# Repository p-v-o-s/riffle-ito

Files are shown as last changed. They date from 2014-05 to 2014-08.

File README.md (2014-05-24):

riffle-ito
=========

The RIFFLE-ito is a lower-functionality and higher cost version of the [Riffle](http://publiclab.org/wiki/riffle) water quality sensor. The Riffle-ito is based on the Atmel328p, and is intended to be compatible with the accessibile and ubiquitous Wiring platform (and, by extension, the Arduino IDE). For a lower-cost, higher-functionalty Riffle that isn't yet compatible with Wiring, please see [here](https://github.com/bgamari/riffle). 

The width and height of the Riffle-ito device allows the device to fit through the mouth of a standard commercially produced plastic water bottle (20 mm). By inserting the Riffle-ito into such a bottle, along with a few AA batteries, and connecting a thermistor and other sensors that poke out through the water bottle cap, a very accessible water quality sensor may be constructed. 

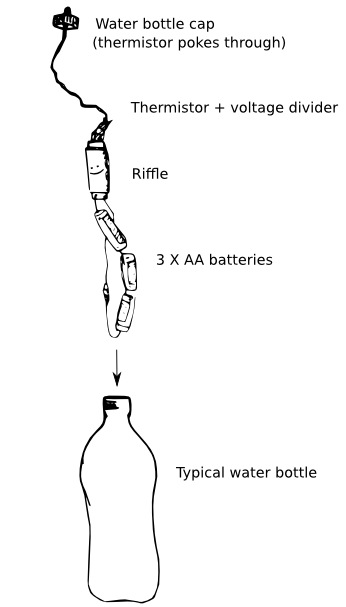
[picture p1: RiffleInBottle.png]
Optional title


Details:

- the Riffle-ito requires an [FTDI cable](https://www.adafruit.com/products/284) in order to be reprogrammed (e.g. Adafruit's [FTDI Friend](https://www.adafruit.com/products/284) or SparkFun's ['FTDI Basic Breakout'](https://www.sparkfun.com/products/9716)), which typically costs $15 or so. One cable can be used for several Riffle-ito senso nodes.
- includes a uSD holder, I2C EEPROM flash memory, and a high-precision real time clock (the DS3231) with coin battery backup
- programmable as an "Arduino UNO" board in the Arduino IDE
- runs at 3.3V / 16 MHz
- includes circuit for monitoring battery level
- the board width (18 mm) and height profile (uses right-angle headers) allows device to be inserted through mouth of standard plastic water bottle (one with 20 mm diameter or greater)
- Rough estimate of the total cost of parts that could be used to log temperature in a water bottle (not including shipping, the water bottle, or an FTDI cable): 38 USD;  a detailed cost estimate is [here](https://docs.google.com/spreadsheets/d/1v0O8HmP8-q_kPunHILv5Io3zThpqvPBZZoY3aYnxRDc/edit#gid=0)
- For a diagram of pin locations and optional configurations, please see this [diagram in PDF format](https://github.com/p-v-o-s/riffle328/blob/master/riffleUsage.pdf)

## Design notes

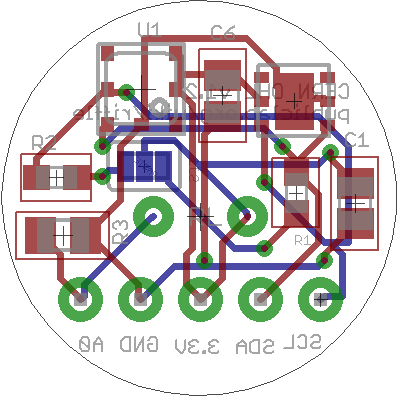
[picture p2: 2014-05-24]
hardware/riffleito-THPL-REVB-board.png

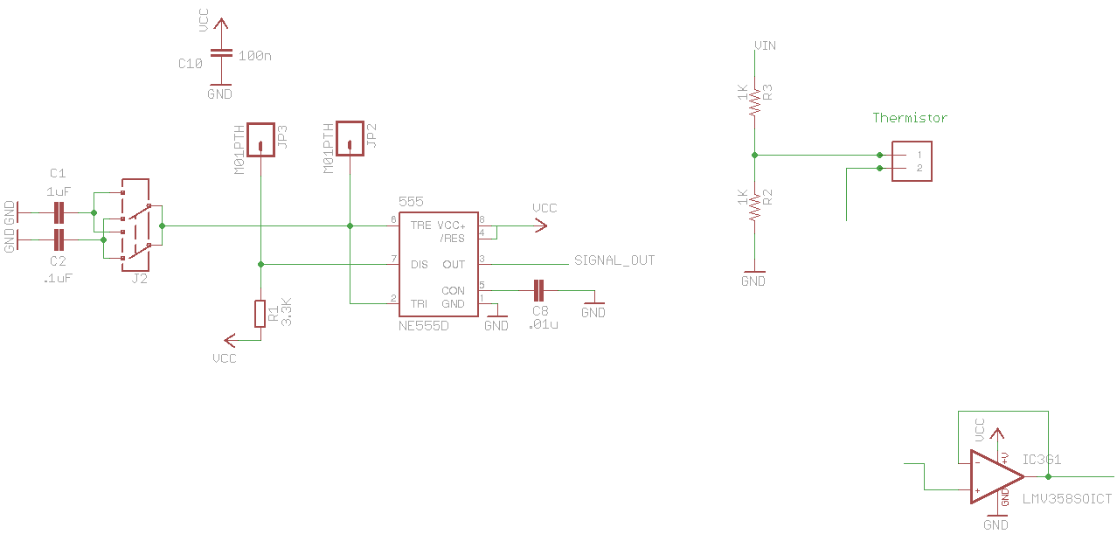
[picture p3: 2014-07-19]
hardware/conduct3-schem.png

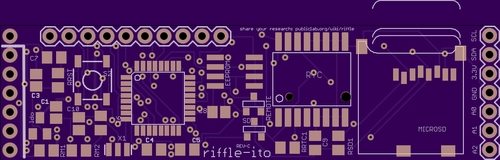
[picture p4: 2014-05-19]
hardware/riffle-ito-revc-osh-front.png

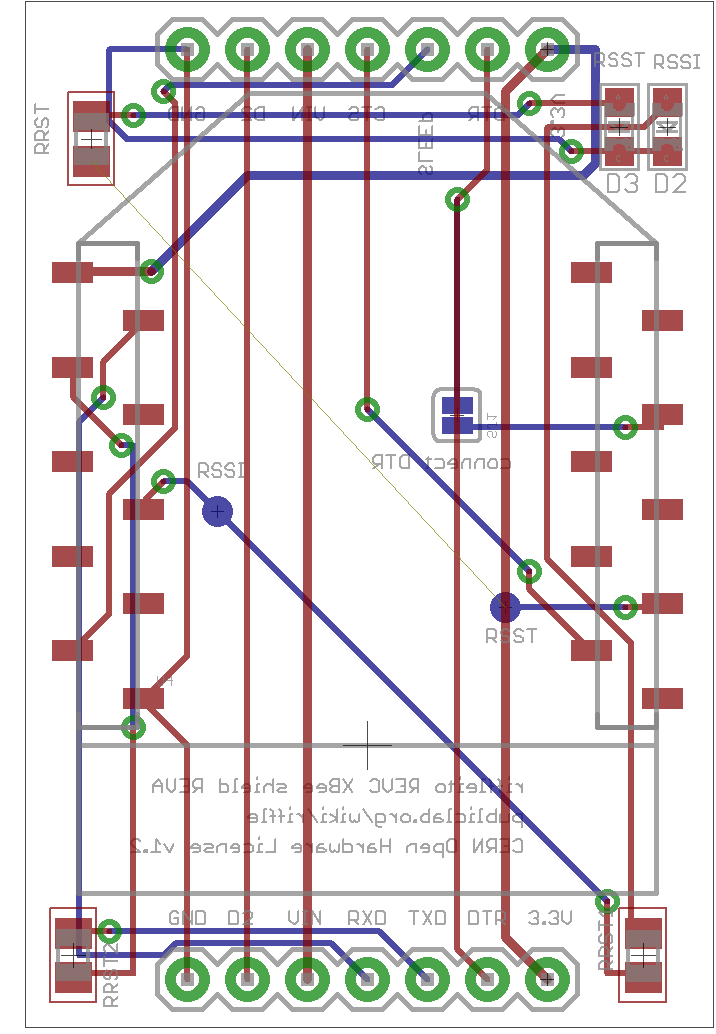
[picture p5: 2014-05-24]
hardware/riffleito-Xbee_REVA-board.png

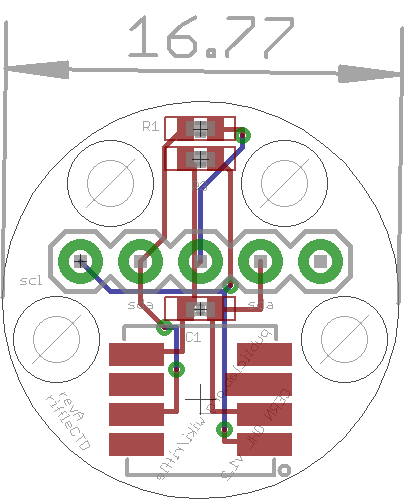
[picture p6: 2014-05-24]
hardware/riffleito-CTD-REVA-board.png

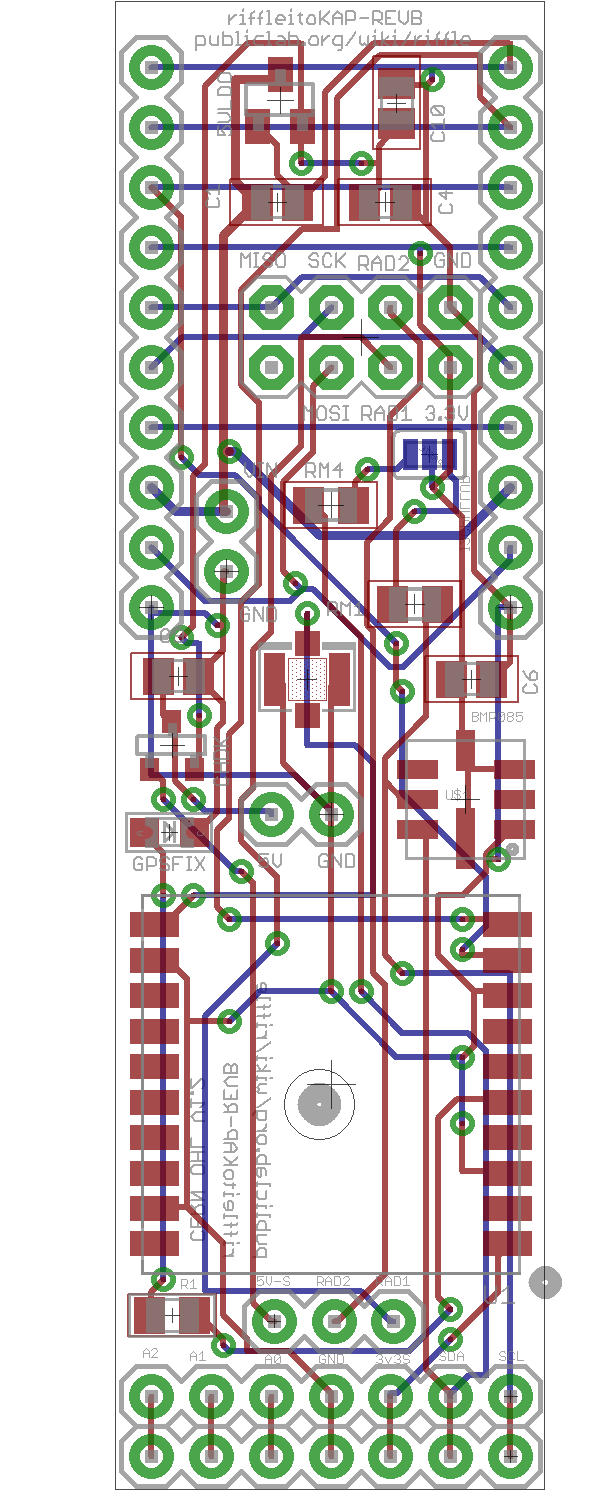
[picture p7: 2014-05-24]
hardware/riffleito-KAP-REVB-board.png

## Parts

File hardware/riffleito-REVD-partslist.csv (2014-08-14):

Part | Value | Device | Package | Description | MF | MPN | OC_FARNELL | OC_NEWARK
BAT | CR1220 | BATTERYBATTERY_12MM_SMT | BATTCON_12MM_SMT | Battery Holders
C1 | 10u | C-EUC0805 | C0805 | CAPACITOR, European symbol
C3 | 10u | C-EUC0805 | C0805 | CAPACITOR, European symbol
C4 | 0.1uF | C-EUC0805 | C0805@1 | CAPACITOR, European symbol
C5 | 0.1uF | C-EUC0805 | C0805@1 | CAPACITOR, European symbol
C6 | .1uF | C-EUC0805 | C0805@1 | CAPACITOR, European symbol
C7 | 0.1uF | C-EUC0805 | C0805@1 | CAPACITOR, European symbol
C8 | .1u | C-EUC0805 | C0805 | CAPACITOR, European symbol
C10 | .1u | C-EUC0805 | C0805 | CAPACITOR, European symbol
CRF | .1u | C-EUC0805 | C0805 | CAPACITOR, European symbol
CSD | .1uF | C-EUC0805 | C0805 | CAPACITOR, European symbol
I2C1 | 10K | R-EU_R0805 | R0805 | RESISTOR, European symbol
I2C2 | 10K | R-EU_R0805 | R0805 | RESISTOR, European symbol
IC1 | ATMEGA328P | MEGA8-AI | TQFP32-08 | MICROCONTROLLER |  | ATMEGA8-16AU | 9171371 | 73M8863
IC2 | 24AA128SN | 24AA128SN | SO-08 | Serial EEPROM | MICROCHIP | 24AA128-I/SN | unknown | 92C6842
IC4 | MCP1700-33 | MCP1700SOT233 | SOT23 | VOLTAGE REGULATOR
JP1 |  | M081X08 | 1X08 | Header 8
JP2 |  | M06SIP | 1X06 | Header 6
JP4 |  | M07 | 1X07 | Header 7
MICROSD | MICROSD | MICROSD | MICROSD | Micro-SD / Transflash card holder with SPI pinout
REMOTE | FDN340P | PMOSSOT23 | SOT-23 | MOS FET
RM1 | 10K | R-EU_R0805 | R0805 | RESISTOR, European symbol
RM2 | 10K | R-EU_R0805 | R0805 | RESISTOR, European symbol
RRST | 10K | R-EU_R0805 | R0805 | RESISTOR, European symbol
RRTC1 | 10K | R-EU_R0805 | R0805 | RESISTOR, European symbol
RSD1 | 10K | R-EU_R0805 | R0805 | RESISTOR, European symbol
RTC | DS3231 | DS3231 | DS3231
RTCINT | SOLDERJUMPERNO | SOLDERJUMPERNO | SJ_2S-NO | Solder Jumper
SD | FDN340P | PMOSSOT23 | SOT-23 | MOS FET
U$1 | M04X2 | M04X2 | 2X4 | .1 header, two rows of four."
X1 | 16 MHz | RESONATORSMD | RESONATOR-SMD | Resonator

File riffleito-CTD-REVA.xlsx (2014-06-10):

Part | Value | Device | Package | Description
C1 | 100 nF | CAP0402-CAP | 0402-CAP | Capacitor
JP2 |  | M05PTH | 1X05 | Header 5
MS5803 | MS5803-14BA | MS5803-14BA | MS5803-14BA
R1 | 10K | RESISTOR0402-RES | 0402-RES | Resistor
R3 | 10K | RESISTOR0402-RES | 0402-RES | Resistor

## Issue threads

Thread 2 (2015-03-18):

### ISSUE TITLE
Make 'Nutrition Facts' label

### ISSUE THREAD

**Issue by dwblair** [p-v-o-s/riffle-ito#2]
![rifflelabel](https://cloud.githubusercontent.com/assets/639760/3027999/30445cfa-e028-11e3-8816-b8fbdc38216b.png)

**Comment by BobStevens** [comment]
perhaps a vintage beverage logo...
![riffle](https://cloud.githubusercontent.com/assets/4740637/3029463/75da4e70-e035-11e3-9c63-8aa23d116dfc.png)
![riffle2](https://cloud.githubusercontent.com/assets/4740637/3032722/72b22f80-e05b-11e3-9458-ed36393352e9.png)

**Comment by dwblair** [comment]
Bob.  You're a genius.  MAJORLY AWESOME.

**Comment by kanarinka** [comment]
![rifflelabel2](https://cloud.githubusercontent.com/assets/1102550/3116949/32e98ee2-e723-11e3-82cc-9f281cf4ee9f.png)
Another label idea!! Let's keep iterating and then we can make a couple and do market research on which label seduces the most citizen scientists :+1:

**Comment by kanarinka** [comment]
![rifflelabel3](https://cloud.githubusercontent.com/assets/1102550/3117523/aab2b39e-e72e-11e3-8b7b-fed8c4b8d51d.png)
And here's one using Bob's font which I like a great deal!

**Comment by kanarinka** [comment]
![rifflelabel4](https://cloud.githubusercontent.com/assets/1102550/3117865/ece08718-e734-11e3-8b70-3ab5bd1f3163.png)
What about this for the water bottle conference stickers?? I'd have to redo it more carefully and not sure if the bleed would work but let me know

**Comment by BobStevens** [comment]
Nice, the font I used is an open font called Lemon by Eduardo Tunni.

**Comment by kanarinka** [comment]
❤️❤️❤️😄

El miércoles, 18 de marzo de 2015, dwblair notifications@github.com
escribió:

> Closed #2 https://github.com/p-v-o-s/riffle-ito/issues/2.
> 
> —
> Reply to this email directly or view it on GitHub
> https://github.com/p-v-o-s/riffle-ito/issues/2#event-258748090.

## 

---

www.kanarinka.com    ||    kanarinka@ikatun.org    ||    617-501-2441

---

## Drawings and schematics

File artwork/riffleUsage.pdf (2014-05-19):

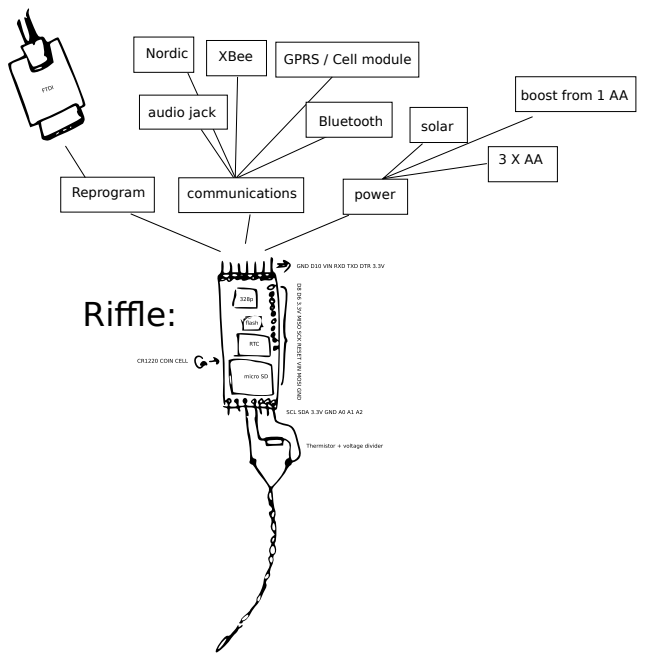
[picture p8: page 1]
Bluetooth; Riffle:; XBee; GPRS / Cell module; power; solar; Reprogram; Nordic; communications; audio jack

boost from 1 AA

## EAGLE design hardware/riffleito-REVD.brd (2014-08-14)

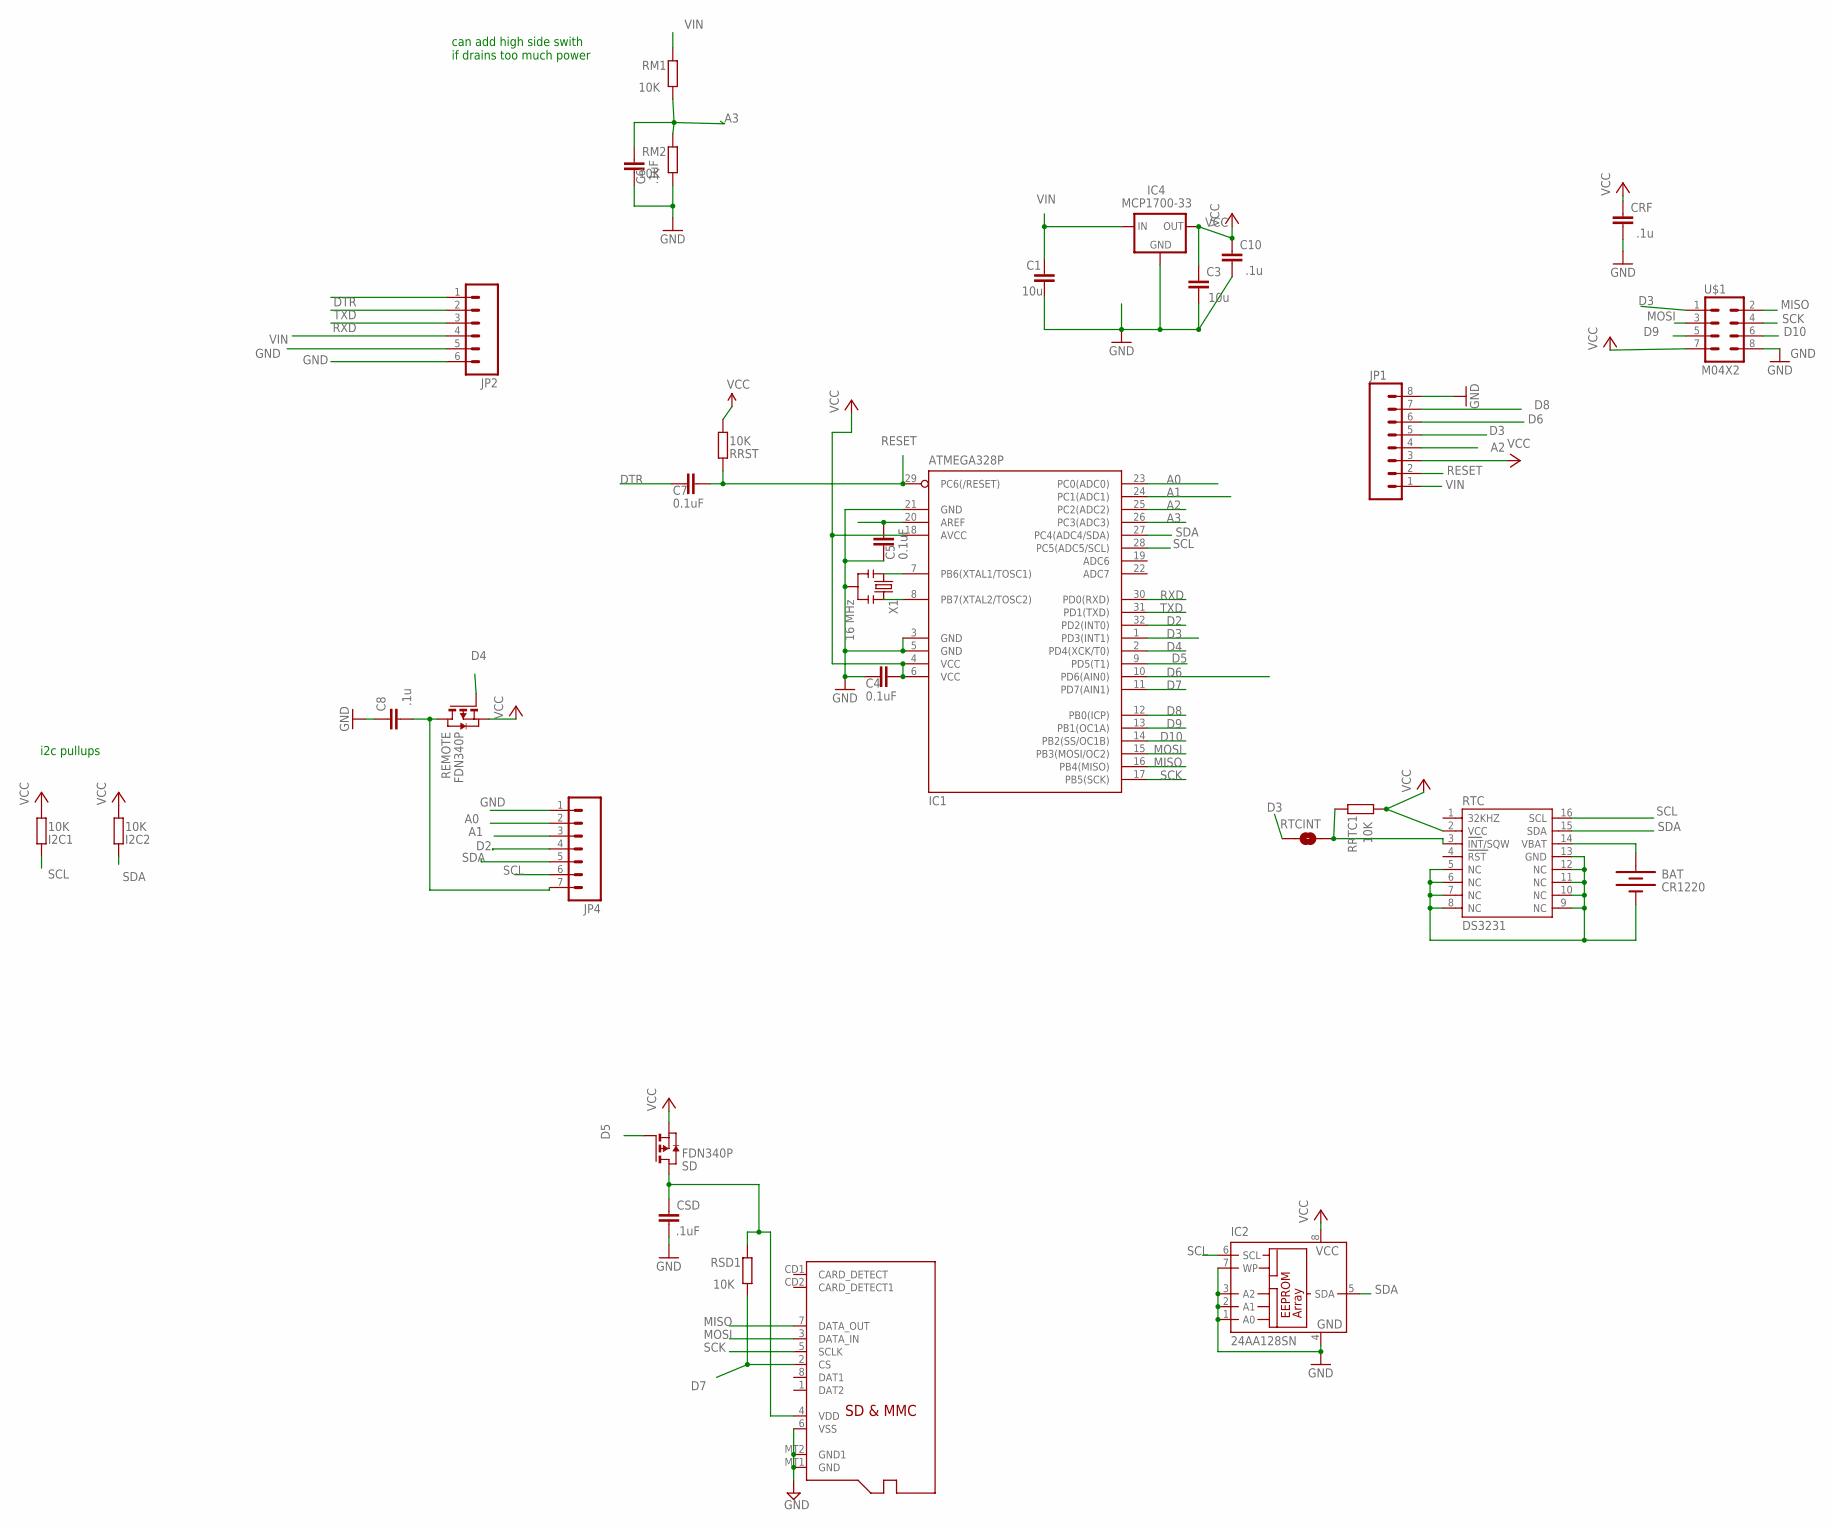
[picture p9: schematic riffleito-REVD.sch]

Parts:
BAT: CR1220; BATTCON_12MM_SMT
C1, C3: 10u; C0805
C4, C5, C7: 0.1uF; C0805@1
C6: .1uF; C0805@1
C8, C10: .1u; C0805
CRF: .1u; C0805
CSD: .1uF; C0805
I2C1, I2C2: 10K; R0805
IC1: ATMEGA328P; TQFP32-08
IC2: 24AA128SN; SO-08
IC4: MCP1700-33; SOT23
JP1: M081X08; 1X08
JP2: M06SIP; 1X06
JP4: M07; 1X07
MICROSD: MICROSD
REMOTE: FDN340P; SOT-23
RM1, RM2: 10K; R0805
RRST: 10K; R0805
RRTC1: 10K; R0805
RSD1: 10K; R0805
RTC: DS3231
RTCINT: SOLDERJUMPERNO; SJ_2S-NO
SD: FDN340P; SOT-23
U$1: M04X2; 2X4
X1: 16 MHz; RESONATOR-SMD

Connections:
A0: IC1.23 (PC0(ADC0)), JP4.2
A1: IC1.24 (PC1(ADC1)), JP4.3
A2: IC1.25 (PC2(ADC2)), JP1.4
A3: C6.2, IC1.26 (PC3(ADC3)), RM1.1, RM2.2
AREF: C5.2, IC1.20 (AREF)
D2: IC1.32 (PD2(INT0)), JP4.4
D3: IC1.1 (PD3(INT1)), JP1.5, RTCINT.2, U$1.1
D4: IC1.2 (PD4(XCK/T0)), REMOTE.3 (G)
D5: IC1.9 (PD5(T1)), SD.3 (G)
D6: IC1.10 (PD6(AIN0)), JP1.6
D7: IC1.11 (PD7(AIN1)), MICROSD.2 (CS), RSD1.1
D8: IC1.12 (PB0(ICP)), JP1.7
D9: IC1.13 (PB1(OC1A)), U$1.5
D10: IC1.14 (PB2(SS/OC1B)), U$1.6
DTR: C7.1, JP2.1
GND: BAT.P$1 (-), C1.2, C3.2, C4.1, C5.1, C6.1, C8.1, C10.2, CRF.2, CSD.2, IC1.3 (GND), IC1.5 (GND), IC1.21 (GND), IC2.1 (A0), IC2.2 (A1), IC2.3 (A2), IC2.4 (GND), IC2.7 (WP), IC4.1 (GND), JP1.8, JP2.5, JP2.6, JP4.1, MICROSD.6 (VSS), MICROSD.MT1 (GND), MICROSD.MT2 (GND1), RM2.1, RTC.5 (NC), RTC.6 (NC), RTC.7 (NC), RTC.8 (NC), RTC.9 (NC), RTC.10 (NC), RTC.11 (NC), RTC.12 (NC), RTC.13 (GND), U$1.8, X1.2
MISO: IC1.16 (PB4(MISO)), MICROSD.7 (DATA_OUT), U$1.2
MOSI: IC1.15 (PB3(MOSI/OC2)), MICROSD.3 (DATA_IN), U$1.3
unnamed: RRTC1.2, RTC.3 (INT/SQW), RTCINT.1
unnamed: IC1.8 (PB7(XTAL2/TOSC2)), X1.3
unnamed: IC1.7 (PB6(XTAL1/TOSC1)), X1.1
unnamed: C8.2, JP4.7, REMOTE.1 (D)
RESET: C7.2, IC1.29 (PC6(/RESET)), JP1.2, RRST.2
RTC_BATT: BAT.P$2 (+), RTC.14 (VBAT)
RXD: IC1.30 (PD0(RXD)), JP2.3
SCK: IC1.17 (PB5(SCK)), MICROSD.5 (SCLK), U$1.4
SCL: I2C1.2, IC1.28 (PC5(ADC5/SCL)), IC2.6 (SCL), JP4.6, RTC.16 (SCL)
SDA: I2C2.2, IC1.27 (PC4(ADC4/SDA)), IC2.5 (SDA), JP4.5, RTC.15 (SDA)
TXD: IC1.31 (PD1(TXD)), JP2.2
VCC: C3.1, C4.2, C10.1, CRF.1, I2C1.1, I2C2.1, IC1.4 (VCC), IC1.6 (VCC), IC1.18 (AVCC), IC2.8 (VCC), IC4.2 (OUT), JP1.3, REMOTE.2 (S), RRST.1, RRTC1.1, RTC.2 (VCC), SD.2 (S), U$1.7
VDD: CSD.1, MICROSD.4 (VDD), RSD1.2, SD.1 (D)
VIN: C1.1, IC4.3 (IN), JP1.1, JP2.4, RM1.2

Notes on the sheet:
can add high side swith if drains too much power
i2c pullups

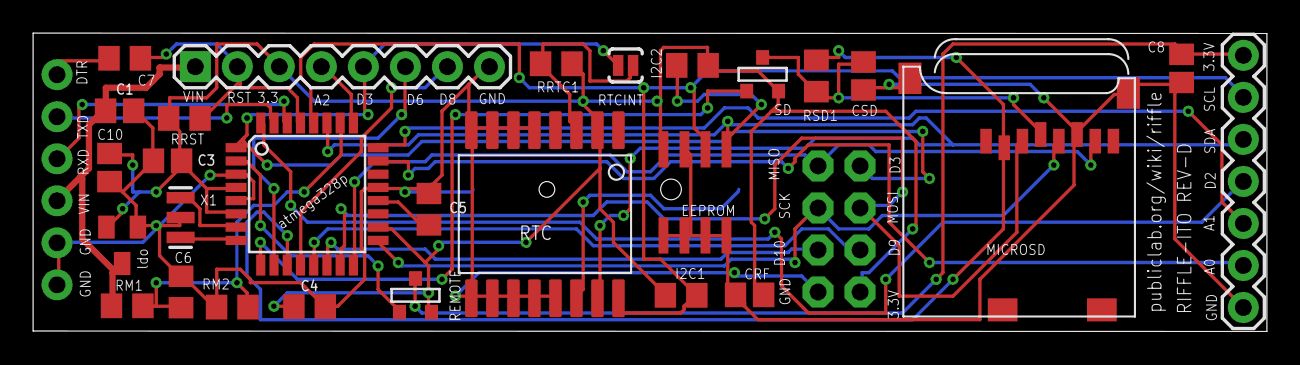
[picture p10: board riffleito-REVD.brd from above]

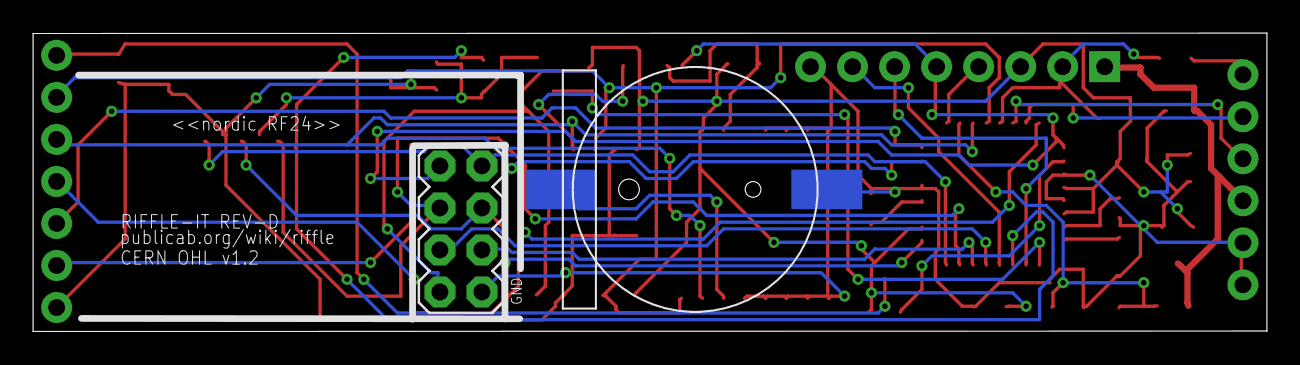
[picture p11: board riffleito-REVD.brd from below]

Board: 2 copper layers, 74.6 x 18.0 mm, 31 parts (2 on the bottom side), 32 nets.

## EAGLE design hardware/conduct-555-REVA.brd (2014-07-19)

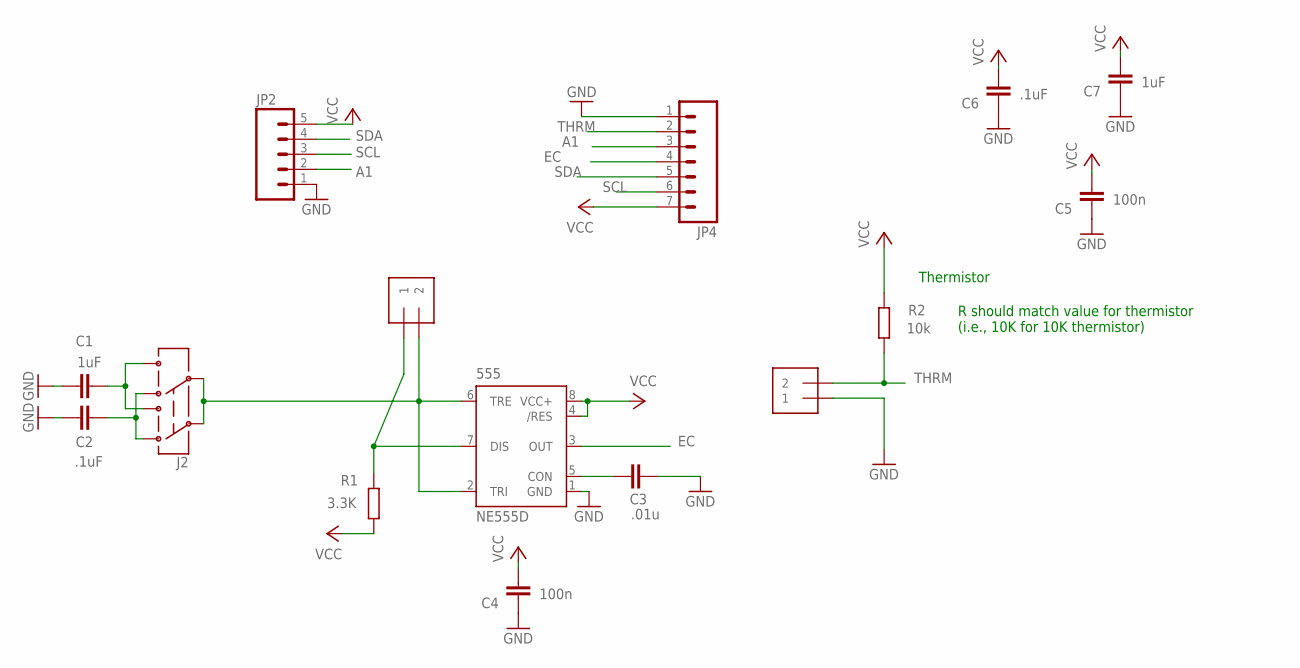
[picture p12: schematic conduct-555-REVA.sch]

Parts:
555: NE555D; SO08@1
C1, C7: 1uF; C0805
C2, C6: .1uF; C0805
C3: .01u; C0805
C4, C5: 100n; C0805
EC: 1X2-3.5MM
J2: AYZ0202
JP2: M05PTH; 1X05
JP4: M07; 1X07
R1: 3.3K; R0805
R2: 10k; R0805
THRM: 1X2-3.5MM

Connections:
A1: JP2.2, JP4.3
EC: 555.3 (OUT), JP4.4
GND: 555.1 (GND), C1.2, C2.2, C3.1, C4.1, C5.1, C6.1, C7.1, JP2.1, JP4.1, THRM.1
N1: 555.2 (TRI), 555.6 (TRE), EC.2, J2.2, J2.5
unnamed: 555.5 (CON), C3.2
unnamed: 555.7 (DIS), EC.1, R1.2
unnamed: C2.1, J2.3 (1), J2.6 (4)
SCL: JP2.3, JP4.6
SDA: JP2.4, JP4.5
THRM: JP4.2, R2.1, THRM.2
VCC: 555.4 (/RES), 555.8 (VCC+), C4.2, C5.2, C6.2, C7.2, JP2.5, JP4.7, R1.1, R2.2
VDD2: C1.1, J2.1 (3), J2.4 (6)

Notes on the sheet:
Thermistor
R should match value for thermistor (i.e., 10K for 10K thermistor)

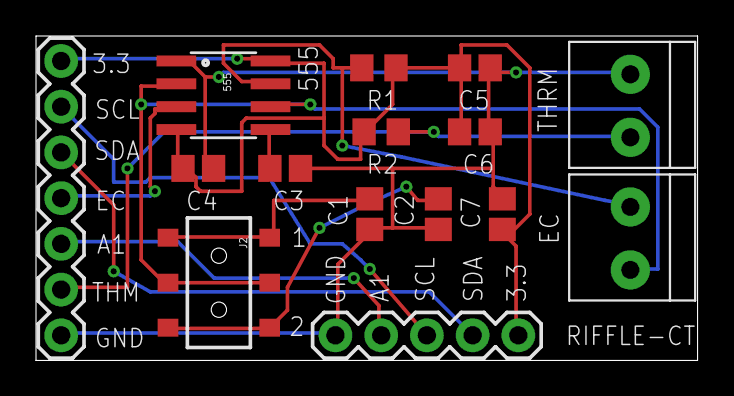
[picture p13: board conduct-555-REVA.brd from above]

Board: 2 copper layers, 36.8 x 18.0 mm, 15 parts (0 on the bottom side), 12 nets.

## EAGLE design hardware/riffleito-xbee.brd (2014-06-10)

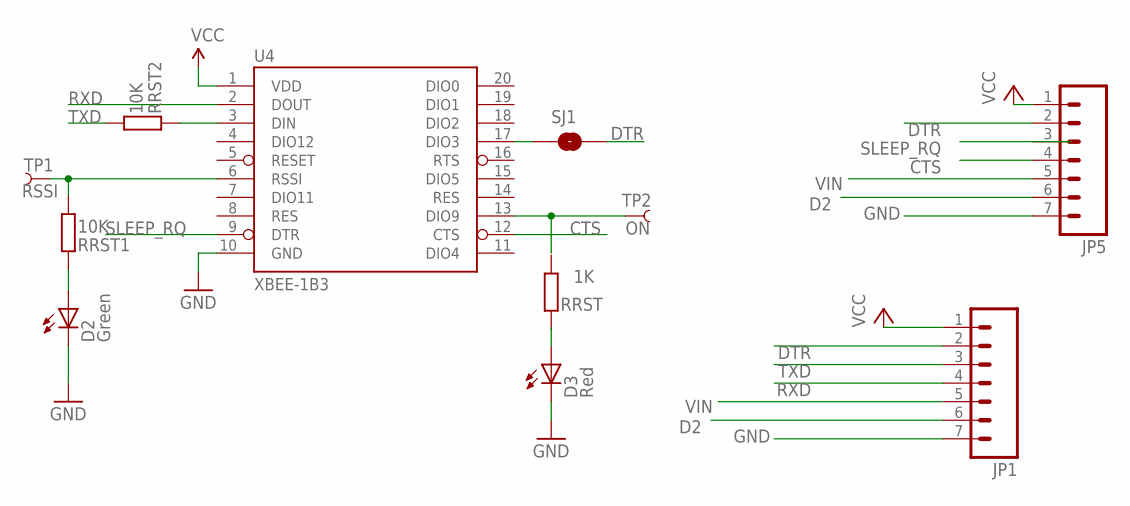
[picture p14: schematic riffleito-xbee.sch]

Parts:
D2: Green; LED-0603
D3: Red; LED-0603
JP1, JP5: M07; 1X07
RRST: 1K; R0805
RRST1, RRST2: 10K; R0805
SJ1: SOLDERJUMPERNC; SJ_2S
TP1: RSSI; PAD.03X.05
TP2: ON; PAD.03X.05
U4: XBEE-1B3; XBEE-SMD

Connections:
CTS: JP5.4, U4.12 (CTS)
D2: JP1.6, JP5.6
DTR: JP1.2, JP5.2, SJ1.2
GND: D2.C, D3.C, JP1.7, JP5.7, U4.10 (GND)
unnamed: TP2.P$1, U4.13 (DIO9)
unnamed: D2.A, RRST1.2
unnamed: RRST1.1, TP1.P$1, U4.6 (RSSI)
unnamed: D3.A, RRST.2
unnamed: RRST2.2, U4.3 (DIN)
unnamed: SJ1.1, U4.17 (DIO3)
RXD: JP1.4, U4.2 (DOUT)
SLEEP_RQ: JP5.3, U4.9 (DTR)
TXD: JP1.3, RRST2.1
VCC: JP1.1, JP5.1, U4.1 (VDD)
VIN: JP1.5, JP5.5

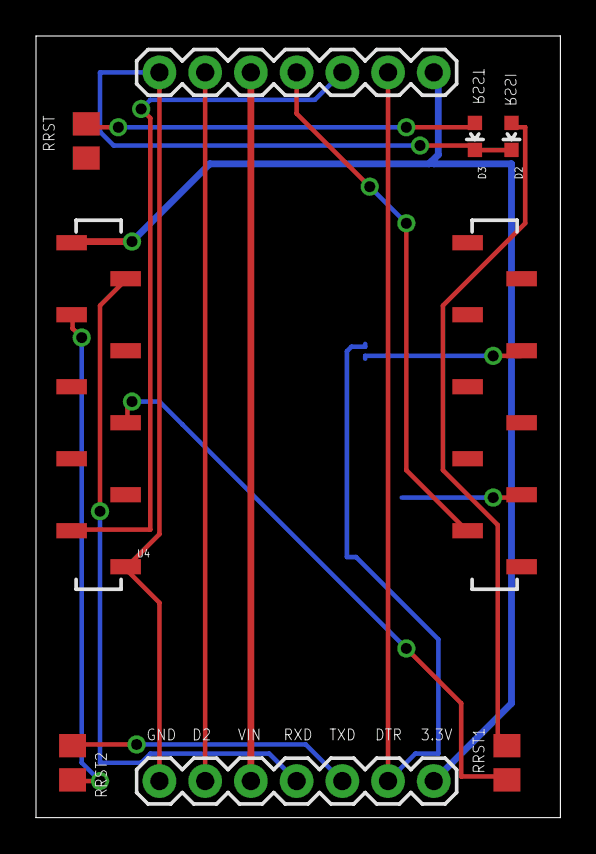
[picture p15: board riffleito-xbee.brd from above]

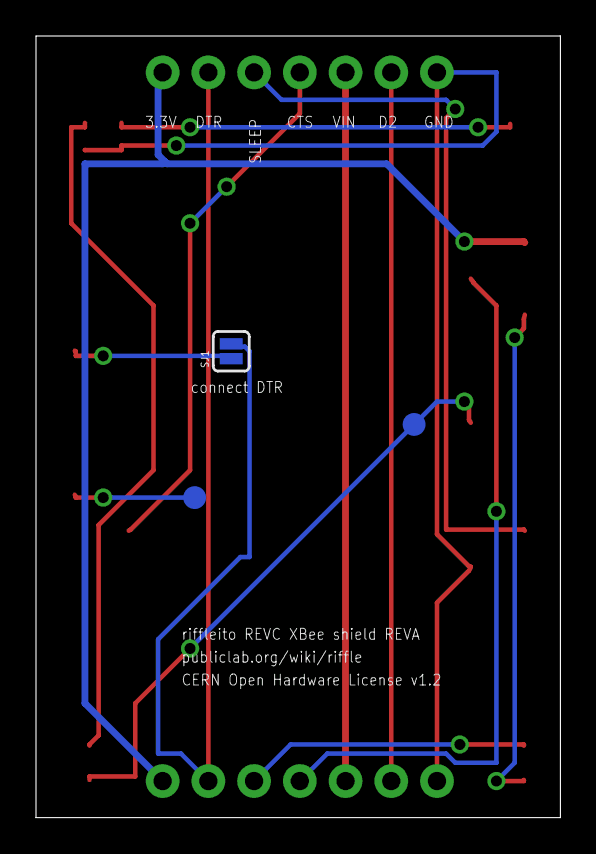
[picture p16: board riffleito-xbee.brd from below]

Board: 2 copper layers, 29.1 x 43.4 mm, 11 parts (3 on the bottom side), 15 nets.

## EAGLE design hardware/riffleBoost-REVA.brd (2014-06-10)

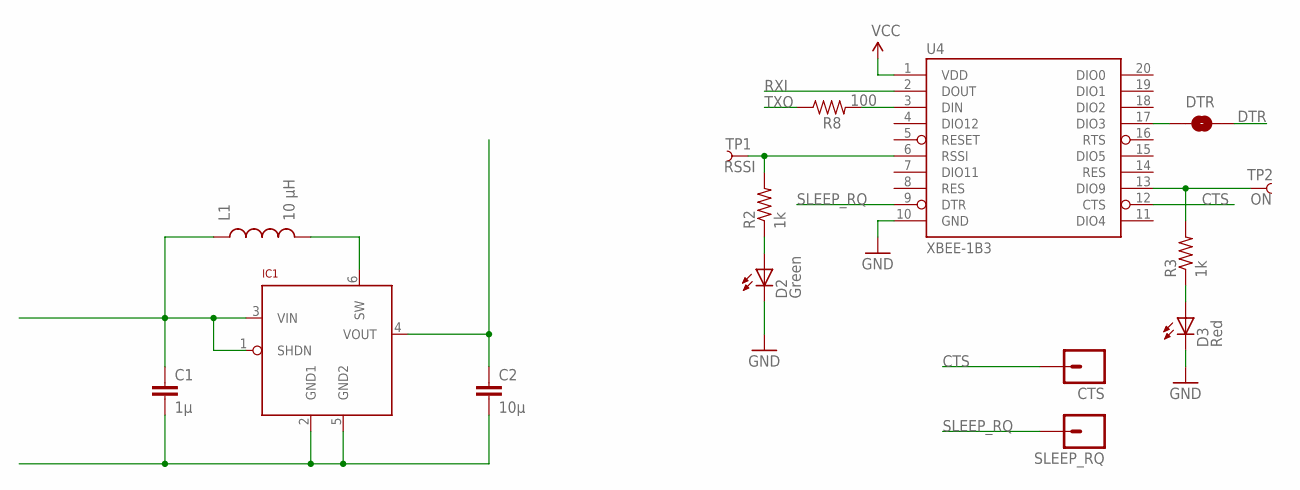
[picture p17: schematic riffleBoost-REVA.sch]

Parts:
C1: 1µ; 0603-CAP
C2: 10µ; 0805
CTS: M01PTH; 1X01
D2: Green; LED-0603
D3: Red; LED-0603
DTR: SOLDERJUMPERNC; SJ_2S
IC1: LTC3525; SC70
L1: 10 µH; 1210
R2, R3: 1k; 0402-RES
R8: 100; 0402-RES
SLEEP_RQ: M01PTH; 1X01
TP1: RSSI; PAD.03X.05
TP2: ON; PAD.03X.05
U4: XBEE-1B3; XBEE-SMD

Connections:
CTS: CTS.1, U4.12 (CTS)
DTR: DTR.2
GND: C1.2, C2.2, D2.C, D3.C, IC1.2 (GND1), IC1.5 (GND2), U4.10 (GND)
unnamed: C1.1, IC1.1 (SHDN), IC1.3 (VIN), L1.1
unnamed: R2.2, TP1.P$1, U4.6 (RSSI)
unnamed: D2.A, R2.1
unnamed: IC1.6 (SW), L1.2
unnamed: R3.2, TP2.P$1, U4.13 (DIO9)
unnamed: D3.A, R3.1
unnamed: R8.2, U4.3 (DIN)
unnamed: DTR.1, U4.17 (DIO3)
RXI: U4.2 (DOUT)
SLEEP_RQ: SLEEP_RQ.1, U4.9 (DTR)
TXO: R8.1
VCC: C2.1, IC1.4 (VOUT), U4.1 (VDD)

Board: 2 copper layers, 15 parts (0 on the bottom side), 12 nets, no tracks yet.

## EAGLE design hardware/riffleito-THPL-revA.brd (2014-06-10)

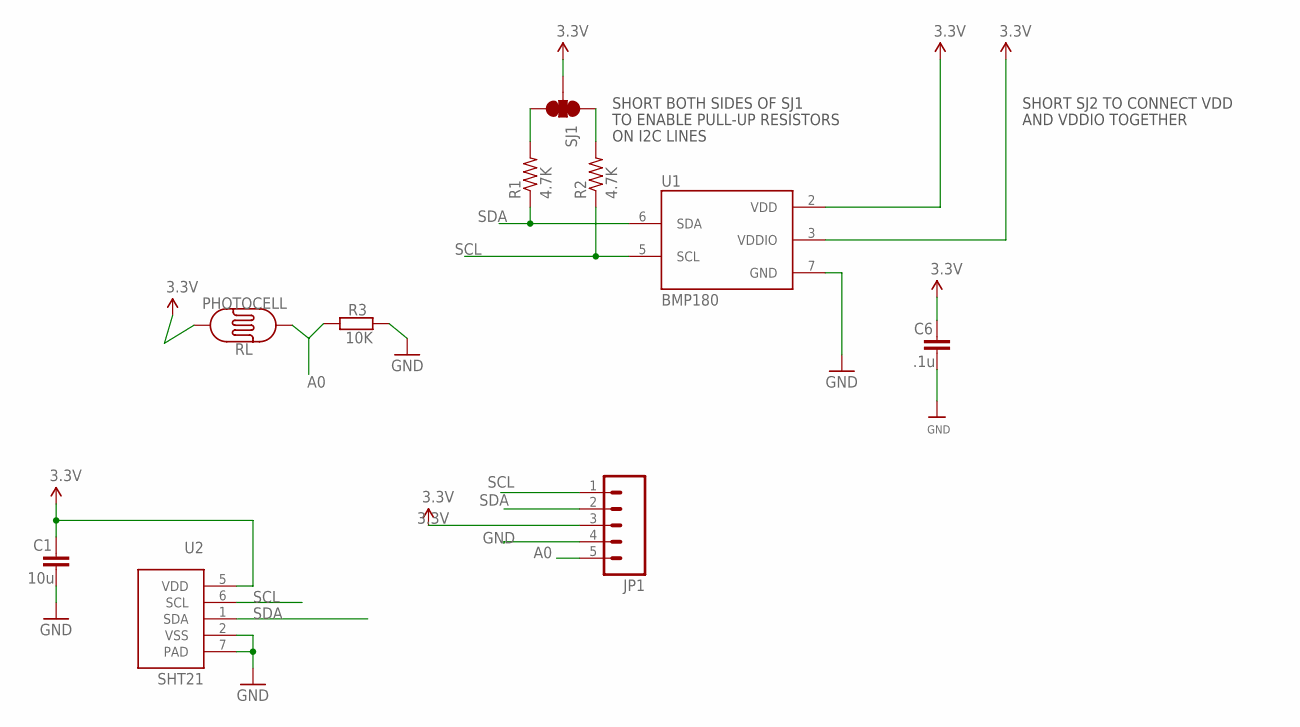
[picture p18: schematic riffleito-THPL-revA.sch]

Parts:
C1: 10u; C0805
C6: .1u; C0805
JP1: M05PTH; 1X05
R1, R2: 4.7K; 0603-RES
R3: 10K; R0805
RL: PHOTOCELL
SJ1: SOLDERJUMPER_2WAYPASTE1&2&3; SJ_3_PASTE1&2&3
U1: BMP180
U2: SHT21; SEN-SENSIRION-SHT2X

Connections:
3.3V: C1.1, C6.1, JP1.3, RL.2, SJ1.2, U1.2 (VDD), U1.3 (VDDIO), U2.5 (VDD)
A0: JP1.5, R3.1, RL.1
GND: C1.2, C6.2, JP1.4, R3.2, U1.7 (GND), U2.2 (VSS), U2.7 (PAD)
unnamed: R1.2, SJ1.3
unnamed: R2.2, SJ1.1
SCL: JP1.1, R2.1, U1.5 (SCL), U2.6 (SCL)
SDA: JP1.2, R1.1, U1.6 (SDA), U2.1 (SDA)

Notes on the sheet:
SHORT BOTH SIDES OF SJ1
TO ENABLE PULL-UP RESISTORS
ON I2C LINES
SHORT SJ2 TO CONNECT VDD
AND VDDIO TOGETHER

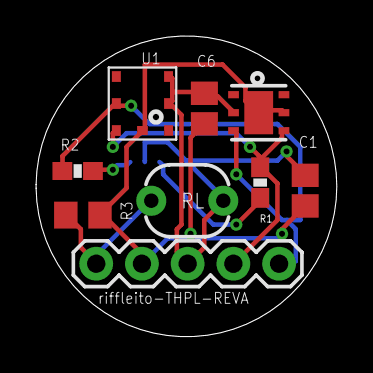
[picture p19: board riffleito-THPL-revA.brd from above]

Board: 2 copper layers, 16.7 x 16.7 mm, 10 parts (1 on the bottom side), 7 nets.

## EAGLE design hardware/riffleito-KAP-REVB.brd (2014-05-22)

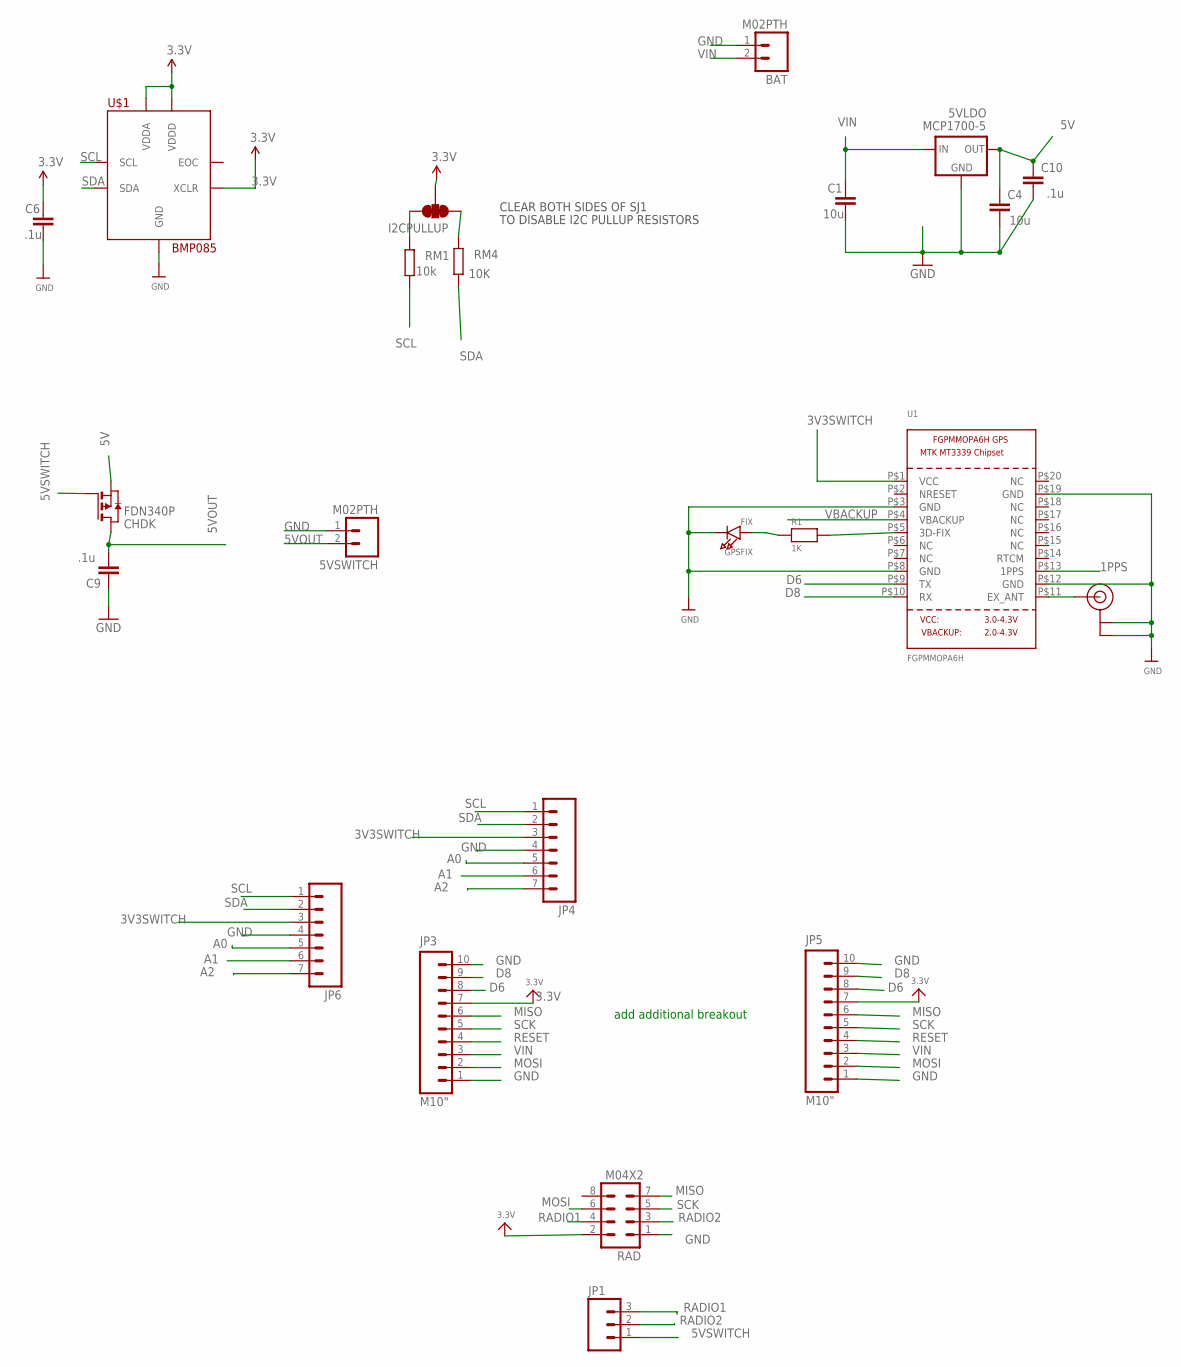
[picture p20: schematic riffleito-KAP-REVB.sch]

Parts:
5VLDO: MCP1700-5; SOT23
5VSWITCH: M02PTH; 1X02
BAT: M02PTH; 1X02
C1, C4: 10u; C0805
C6, C9, C10: .1u; C0805
CHDK: FDN340P; SOT-23
GPSFIX: FIX; CHIPLED_0805
I2CPULLUP: SOLDERJUMPER_2WAYPASTE1&2&3; SJ_3_PASTE1&2&3
JP1: M03PTH; 1X03
JP3, JP5: M10"; 1X10
JP4, JP6: M07; 1X07
R1: 1K; 0805
RAD: M04X2; 2X4
RM1: 10k; R0805
RM4: 10K; R0805
U1: FGPMMOPA6H
U$1: BMP085
U$20: U.FL

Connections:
1PPS: U1.P$13 (1PPS)
3.3V: C6.1, I2CPULLUP.2, JP3.7, JP5.7, RAD.2, U$1.P$3 (VDDA), U$1.P$4 (VDDD), U$1.P$8 (XCLR)
3V3SWITCH: JP4.3, JP6.3, U1.P$1 (VCC)
5V: 5VLDO.2 (OUT), C4.1, C10.1, CHDK.2 (S)
5VOUT: 5VSWITCH.2, C9.2, CHDK.1 (D)
5VSWITCH: CHDK.3 (G), JP1.1
A0: JP4.5, JP6.5
A1: JP4.6, JP6.6
A2: JP4.7, JP6.7
D6: JP3.8, JP5.8, U1.P$9 (TX)
D8: JP3.9, JP5.9, U1.P$10 (RX)
GND: 5VLDO.1 (GND), 5VSWITCH.1, BAT.1, C1.2, C4.2, C6.2, C9.1, C10.2, GPSFIX.C, JP3.1, JP3.10, JP4.4, JP5.1, JP5.10, JP6.4, RAD.1, U1.P$3 (GND), U1.P$8 (GND), U1.P$12 (GND), U1.P$19 (GND), U$1.P$1 (GND), U$20.P$1 (GND), U$20.P$2 (GND)
MISO: JP3.6, JP5.6, RAD.7
MOSI: JP3.2, JP5.2, RAD.6
unnamed: GPSFIX.A, R1.1
unnamed: R1.2, U1.P$5 (3D-FIX)
unnamed: I2CPULLUP.3, RM1.2
unnamed: U1.P$11 (EX_ANT), U$20.P$3 (SIGNAL)
unnamed: I2CPULLUP.1, RM4.2
RADIO1: JP1.3, RAD.4
RADIO2: JP1.2, RAD.3
RESET: JP3.4, JP5.4
SCK: JP3.5, JP5.5, RAD.5
SCL: JP4.1, JP6.1, RM1.1, U$1.P$6 (SCL)
SDA: JP4.2, JP6.2, RM4.1, U$1.P$7 (SDA)
VBACKUP: U1.P$4 (VBACKUP)
VIN: 5VLDO.3 (IN), BAT.2, C1.1, JP3.3, JP5.3

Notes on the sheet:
CLEAR BOTH SIDES OF SJ1
TO DISABLE I2C PULLUP RESISTORS
add additional breakout


Board: 2 copper layers, 18.2 x 63.0 mm, 23 parts (1 on the bottom side), 25 nets.

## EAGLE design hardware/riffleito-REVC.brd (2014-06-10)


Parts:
BAT: CR1220; BATTCON_12MM_SMT
C1, C3: 10u; C0805
C4, C5, C7: 0.1uF; C0805@1
C6, C9: .1uF; C0805@1
C8, C10: .1u; C0805
IC1: ATMEGA328P; TQFP32-08
IC2: 24AA128SN; SO-08
IC4: MCP1700-33; SOT23
JP1, JP4: M07; 1X07
JP5: M10"; 1X10
MICROSD: MICROSD
REMOTE: FDN340P; SOT-23
RM1, RM2: 10K; R0805
RRST: 10K; R0805
RRTC1: 10K; R0805
RSD1: 10K; R0805
RTC: DS3231
RTCINT: SOLDERJUMPERNO; SJ_2S-NO
S2: Reset; TACTILE_SWITCH_SMD
SD: FDN340P; SOT-23
X1: 16 MHz; RESONATOR-SMD

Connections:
A0: IC1.23 (PC0(ADC0)), JP4.5
A1: IC1.24 (PC1(ADC1)), JP4.6
A2: IC1.25 (PC2(ADC2)), JP4.7
A3: C6.2, IC1.26 (PC3(ADC3)), RM1.1, RM2.2
AREF: C5.2, IC1.20 (AREF)
D2: IC1.32 (PD2(INT0)), JP1.6
D3: IC1.1 (PD3(INT1)), RTCINT.2
D4: IC1.2 (PD4(XCK/T0)), REMOTE.3 (G)
D5: IC1.9 (PD5(T1)), SD.3 (G)
D6: IC1.10 (PD6(AIN0)), JP5.8
D7: IC1.11 (PD7(AIN1)), MICROSD.2 (CS), RSD1.1
D8: IC1.12 (PB0(ICP)), JP5.9
D9: IC1.13 (PB1(OC1A))
D10: IC1.14 (PB2(SS/OC1B))
DTR: C7.1, JP1.2
GND: BAT.P$1 (-), C1.2, C3.2, C4.1, C5.1, C6.1, C8.1, C9.1, C10.2, IC1.3 (GND), IC1.5 (GND), IC1.21 (GND), IC2.1 (A0), IC2.2 (A1), IC2.3 (A2), IC2.4 (GND), IC2.7 (WP), IC4.1 (GND), JP1.7, JP4.4, JP5.1, JP5.10, MICROSD.6 (VSS), MICROSD.MT1 (GND), MICROSD.MT2 (GND1), RM2.1, RTC.5 (NC), RTC.6 (NC), RTC.7 (NC), RTC.8 (NC), RTC.9 (NC), RTC.10 (NC), RTC.11 (NC), RTC.12 (NC), RTC.13 (GND), S2.1, S2.2, X1.2
MISO: IC1.16 (PB4(MISO)), JP5.6, MICROSD.7 (DATA_OUT)
MOSI: IC1.15 (PB3(MOSI/OC2)), JP5.2, MICROSD.3 (DATA_IN)
unnamed: IC1.8 (PB7(XTAL2/TOSC2)), X1.3
unnamed: IC1.7 (PB6(XTAL1/TOSC1)), X1.1
RESET: C7.2, IC1.29 (PC6(/RESET)), JP5.4, RRST.2, S2.3, S2.4
RTCINT: RRTC1.2, RTC.3 (INT/SQW), RTCINT.1
RTC_BATT: BAT.P$2 (+), RTC.14 (VBAT)
RXD: IC1.30 (PD0(RXD)), JP1.4
SCK: IC1.17 (PB5(SCK)), JP5.5, MICROSD.5 (SCLK)
SCL: IC1.28 (PC5(ADC5/SCL)), IC2.6 (SCL), JP4.1, RTC.16 (SCL)
SDA: IC1.27 (PC4(ADC4/SDA)), IC2.5 (SDA), JP4.2, RTC.15 (SDA)
TXD: IC1.31 (PD1(TXD)), JP1.3
VCC: C3.1, C4.2, C8.2, C10.1, IC1.4 (VCC), IC1.6 (VCC), IC1.18 (AVCC), IC2.8 (VCC), IC4.2 (OUT), JP1.1, JP4.3, JP5.7, REMOTE.1 (D), REMOTE.2 (S), RRST.1, RRTC1.1, RTC.2 (VCC), SD.2 (S)
VDD: C9.2, MICROSD.4 (VDD), RSD1.2, SD.1 (D)
VIN: C1.1, IC4.3 (IN), JP1.5, JP5.3, RM1.2

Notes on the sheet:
can add high side swith if drains too much power



Board: 2 copper layers, 66.8 x 18.0 mm, 28 parts (3 on the bottom side), 29 nets.

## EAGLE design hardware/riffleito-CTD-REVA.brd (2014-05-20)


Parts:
C1: 100 nF; 0402-CAP
JP2: M05PTH; 1X05
MS5803: MS5803-14BA
R1, R3: 10K; 0402-RES

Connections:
+3V3: C1.1, JP2.3, MS5803.VDD, R1.1, R3.1
A0: JP2.5
GND: C1.2, JP2.4, MS5803.GND
SCL: JP2.1, MS5803.SCLK, R1.2
SDA: JP2.2, MS5803.SDA, R3.2

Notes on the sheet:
I2C Address
GND = 0x77
Interface
VDD = I2C
VDD = 0x76
GND = SPI
Do not leave open for I2C
Do not leave open
Must be open for SPI
MS5803
©2013 Ayerware Publishing
MS5803 Pressure Sensor Board
Do not populate R1 and R2 for SPI - These are I2C pull up resistors.
(default)
I2C PULLUPS -- NOT NEEDED IF PLACE PULLUPS ELSEWHERE (Like on main logic board)


Board: 2 copper layers, 16.8 x 16.8 mm, 5 parts (0 on the bottom side), 4 nets.

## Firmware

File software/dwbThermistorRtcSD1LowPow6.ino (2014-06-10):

#include <JeeLib.h>

 ISR(WDT_vect) { Sleepy::watchdogEvent(); }
 
 
 #define outFileName "testDWB9.csv"
 
#define BATTERYPIN A3

 // which analog pin to connect
#define THERMISTORPIN A2       
// resistance at 25 degrees C
#define THERMISTORNOMINAL 10000      
// temp. for nominal resistance (almost always 25 C)
#define TEMPERATURENOMINAL 25   
// how many samples to take and average, more takes longer
// but is more 'smooth'
#define NUMSAMPLES 5
// The beta coefficient of the thermistor (usually 3000-4000)
#define BCOEFFICIENT 3950
// the value of the 'other' resistor
#define SERIESRESISTOR 10000    

#define DEBUG F

#include <Wire.h>

int samples[NUMSAMPLES];
int led = 6;

#include <SPI.h>
#include <SD.h>

#include <RTClib.h>
#include <RTC_DS3231.h>

RTC_DS3231 RTC;


// On the Ethernet Shield, CS is pin 4. Note that even if it's not
// used as the CS pin, the hardware CS pin (10 on most Arduino boards,
// 53 on the Mega) must be left as an output or the SD library
// functions will not work.
const int chipSelect = 7;    
int SDpower = 5;
int sensorPower = 4;


File dataFile;


 
void setup(void) {
  
  pinMode(SDpower,OUTPUT);
  pinMode(sensorPower,OUTPUT);
  digitalWrite(SDpower,LOW);
  digitalWrite(sensorPower,LOW);
  
   //initialize the SD card
  
  Serial.print("Initializing SD card...");
  // make sure that the default chip select pin is set to
  // output, even if you don't use it:
  pinMode(SS, OUTPUT);
  
  // see if the card is present and can be initialized:
  if (!SD.begin(chipSelect)) {
    Serial.println("Card failed, or not present");
    // don't do anything more:
    while (1) ;
  }
  Serial.println("card initialized.");
  
  //shut down the SD and the sensor -- HIGH is off
  //digitalWrite(SDpower,HIGH);
 // digitalWrite(sensorPower,HIGH);
  
  pinMode(led, OUTPUT); 
  
  // for i2c for RTC
  Wire.begin();
  RTC.begin();
  
  Serial.begin(9600);
  //analogReference(EXTERNAL);

  
  
  
  // check on the RTC
  if (! RTC.isrunning()) {
      Serial.println("RTC is NOT running!");
      // following line sets the RTC to the date & time this sketch was compiled
      RTC.adjust(DateTime(__DATE__, __TIME__));
    }
  
    DateTime now = RTC.now();
    DateTime compiled = DateTime(__DATE__, __TIME__);
    if (now.unixtime() < compiled.unixtime()) {
      //Serial.println("RTC is older than compile time!  Updating");
      RTC.adjust(DateTime(__DATE__, __TIME__));
    }
    
  
  //digitalWrite(SDpower,LOW);
  //digitalWrite(sensorPower,LOW);
  
  
   // Open up the file we're going to log to!
  dataFile = SD.open(outFileName, FILE_WRITE);
  if (! dataFile) {
    Serial.println("error opening datalog.txt");
    // Wait forever since we cant write data
    while (1) ;
  }
  
}
 
void loop(void) {
    
  
  DateTime now = RTC.now();
  
  //get the onboard temp from the RTC
  //RTC.forceTempConv(true);  //DS3231 does this every 64 seconds, we are simply testing the function here
    float RTCTemp = RTC.getTempAsFloat();
  
  
   long unixNow = now.unixtime();
   //bSerial.println(now.unixtime());
   
    
  
   
  // delay(1000);
   
  uint8_t i;
  float average;
 
  // take N samples in a row, with a slight delay
  for (i=0; i< NUMSAMPLES; i++) {
   samples[i] = analogRead(THERMISTORPIN);
   delay(10);
  }
 
  // average all the samples out
  average = 0;
  for (i=0; i< NUMSAMPLES; i++) {
     average += samples[i];
  }
  average /= NUMSAMPLES;
 
  Serial.print("Average analog reading "); 
  Serial.println(average);
 
  // convert the value to resistance
  average = 1023 / average - 1;
  average = SERIESRESISTOR / average;
  Serial.print("Thermistor resistance "); 
  Serial.println(average);
 
  float steinhart;
  steinhart = average / THERMISTORNOMINAL;     // (R/Ro)
  steinhart = log(steinhart);                  // ln(R/Ro)
  steinhart /= BCOEFFICIENT;                   // 1/B * ln(R/Ro)
  steinhart += 1.0 / (TEMPERATURENOMINAL + 273.15); // + (1/To)
  steinhart = 1.0 / steinhart;                 // Invert
  steinhart -= 273.15;                         // convert to C
 
  Serial.print("Temperature "); 
  Serial.print(steinhart);
  Serial.println(" *C");
 
 
// get the battery level
int batteryLevel = analogRead(BATTERYPIN);

    
 // write to sd card
 

  
  float temp10=steinhart*10;
  int temp10int=(int) temp10;
  
  int onboardTempInt = (int) RTCTemp*10;
  
  
  // make a string for assembling the data to log:
  String dataString = "";
  
  dataString += String(unixNow);
  dataString +=",";
  
  dataString += onboardTempInt;
  
  //dataString += String(unixNow);
  dataString+=",";
  
    
  //Serial.print(steinhart);
  dataString += String(temp10int);
  dataString+=",";
    
  dataString += String(batteryLevel);
   //no final comma needed
 
  //write the string to the card
  dataFile.println(dataString);


  
  // print to the serial port too:
  Serial.println(dataString);
  
  // The following line will 'save' the file to the SD card after every
  // line of data - this will use more power and slow down how much data
  // you can read but it's safer! 
  // If you want to speed up the system, remove the call to flush() and it
  // will save the file only every 512 bytes - every time a sector on the 
  // SD card is filled with data.
  dataFile.flush();
// dataFile.close(); //<--- may be unnecessary
 
 
 //shut down the SD and the sensor
  //digitalWrite(SDpower,HIGH);
  //digitalWrite(sensorPower,HIGH);
  
//indicate end of session

    digitalWrite(led, HIGH);
    delay(100);
    digitalWrite(led,LOW);
    
  Sleepy::loseSomeTime(2000); //-- will interfere with serial, so don't use when debugging 
  //delay (2000); // use when debugging -- loseSomeTime does goofy things w/ serial
  
  
}

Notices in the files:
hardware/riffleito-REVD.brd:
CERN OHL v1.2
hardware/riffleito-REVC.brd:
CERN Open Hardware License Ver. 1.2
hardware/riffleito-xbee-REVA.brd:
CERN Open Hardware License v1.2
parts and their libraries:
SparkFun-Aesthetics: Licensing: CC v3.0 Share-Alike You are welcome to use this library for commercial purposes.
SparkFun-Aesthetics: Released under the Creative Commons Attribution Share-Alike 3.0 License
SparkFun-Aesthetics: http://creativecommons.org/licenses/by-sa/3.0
